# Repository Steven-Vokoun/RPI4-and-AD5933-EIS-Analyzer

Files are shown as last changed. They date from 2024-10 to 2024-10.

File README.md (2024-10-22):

# RPI4 and AD5933 EIS Analyzer
Overview:
- Mostly functioning but needs improvements.
- Libraries for AD5933 and MUX's working at this time.
- GUI utilizes custom tkinter.
- Fitting utilized "Impedance" python library (planning to update for robustness)
- Automatic gain switching methods implemented, but has bugs

Improvements I need to make in the future:
- Implementation of the internal 5x switchable gains
- Shift screen off to the left hand side of the enclosure, so then the power supply can be placed right next to the analog board.  Also put filtering on the i2c lines.
- Configuration of 3 electrode switching with a double pole relay instead to completely get it out of the circuit
- Have an external calibration board to account for lead inductance and capacitance
- Add a warning for when the output is hitting supply rails

Future Goals:
- Switch off of a RPI, to a lower level board for lower power consumption
- Shrink the device
- Make my own battery management board

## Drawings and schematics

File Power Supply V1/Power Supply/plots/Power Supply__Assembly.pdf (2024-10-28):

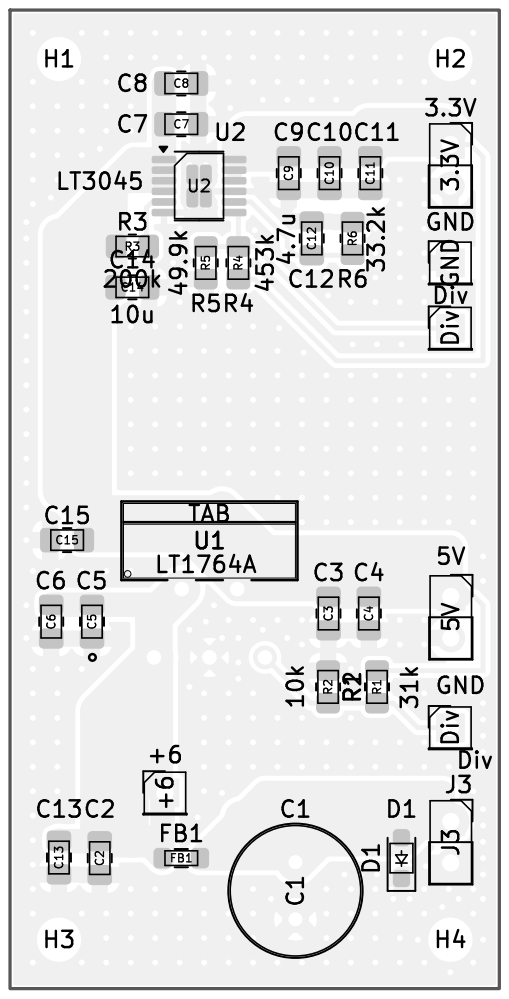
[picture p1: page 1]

Id: 1/1 Title: File: Power Supply.kicad_pcb Sheet:

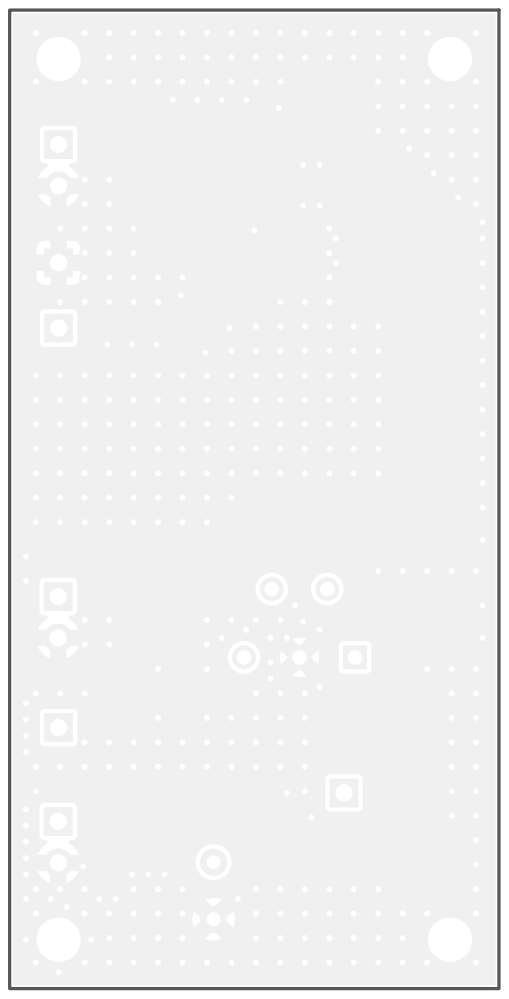
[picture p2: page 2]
D Date: KiCad; E.D.A. 8.0.2 Size: A4; Rev:

Id: 1/1 Title: File: Power Supply.kicad_pcb Sheet:

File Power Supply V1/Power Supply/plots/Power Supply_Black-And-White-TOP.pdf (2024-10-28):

FB1 | C4 C9 1 | 2 | 3 | 4 | 5 | 6 1 | 2 | 3 | 4 | 5 | 6 ABCD | ABCD Date: KiCad | E.D.A. 8.0.2 Size: A4 | Rev:


Id: 1/1 Title: File: Power Supply.kicad_pcb Sheet:

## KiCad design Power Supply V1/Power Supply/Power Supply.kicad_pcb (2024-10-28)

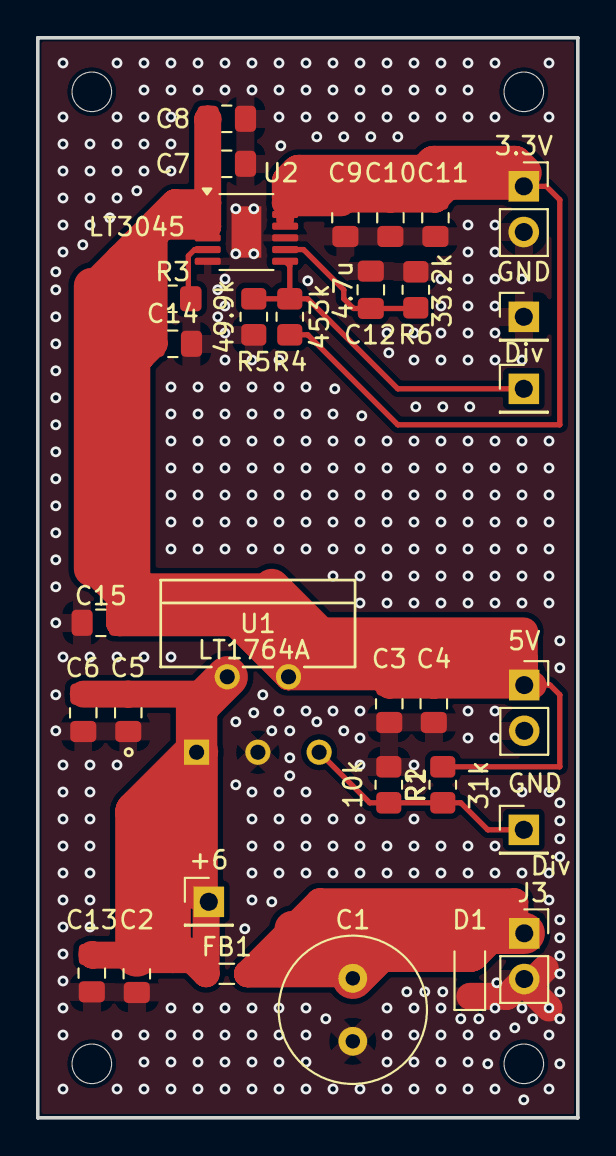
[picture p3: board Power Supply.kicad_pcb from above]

Board: 2 copper layers, 30.0 x 60.0 mm, 36 parts (0 on the bottom side), 9 nets.

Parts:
3.3V, 5V: Conn_01x02_Pin; PinSocket_1x02_P2.54mm_Vertical
+6: Conn_01x01_Pin; PinHeader_1x01_P2.54mm_Vertical
C1: 100u; C_Radial_D8.0mm_H11.5mm_P3.50mm
C2, C3, C8, C13: 22u; C_0805_2012Metric_Pad1.18x1.45mm_HandSolder
C4, C6, C7, C11: .1u; C_0805_2012Metric_Pad1.18x1.45mm_HandSolder
C5, C9, C10, C14, C15: 10u; C_0805_2012Metric_Pad1.18x1.45mm_HandSolder
C12: 4.7u; C_0805_2012Metric_Pad1.18x1.45mm_HandSolder
D1: CDSOD323-To8; D_SOD-323_HandSoldering
Div: Conn_01x01_Pin; PinHeader_1x01_P2.54mm_Vertical
Div#2: Conn_01x01_Pin; PinHeader_1x01_P2.54mm_Vertical
FB1: Ferrite; L_0805_2012Metric_Pad1.05x1.20mm_HandSolder
GND: Conn_01x01_Pin; PinHeader_1x01_P2.54mm_Vertical
H1, H2, H3, H4: MountingHole; MountingHole_2.2mm_M2
J3: Conn_01x02_Pin; PinSocket_1x02_P2.54mm_Vertical
R1: 31k; R_0805_2012Metric_Pad1.20x1.40mm_HandSolder
R2: 10k; R_0805_2012Metric_Pad1.20x1.40mm_HandSolder
R3: 200k; R_0805_2012Metric_Pad1.20x1.40mm_HandSolder
R4: 453k; R_0805_2012Metric_Pad1.20x1.40mm_HandSolder
R5: 49.9k; R_0805_2012Metric_Pad1.20x1.40mm_HandSolder
R6: 33.2k; R_0805_2012Metric_Pad1.20x1.40mm_HandSolder
U1: LT1764A; TO220-5_T_LIT
U2: LT3045; MSOP-12-1EP_3x4mm_P0.65mm_EP1.65x2.85mm

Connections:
+3.3V: 3.3V.1, C9.1, C10.1, C11.1, R4.1, U2.10 (OUTS), U2.11 (OUT), U2.12 (OUT)
+5V: 5V.1, C3.1, C4.1, C7.1, C8.1, C14.1, C15.1, R1.1, R3.1, U1.4 (OUT), U2.1 (IN), U2.2 (IN), U2.3 (IN), U2.4 (EN/UV)
+6V: +6.1, C2.1, C5.1, C6.1, C13.1, FB1.2, U1.1 (*SHDN), U1.2 (IN)
/Div_1: Div.1, R1.2, R2.1, U1.5 (SENSE/ADJ)
/Div_2: Div#2.1, R4.2, R5.1, U2.7 (PGFB)
GND: 3.3V.2, 5V.2, C1.2, C2.2, C3.2, C4.2, C5.2, C6.2, C7.2, C8.2, C9.2, C10.2, C11.2, C12.2, C13.2, C14.2, C15.2, D1.1 (A1), GND.1, J3.2, R2.2, R5.2, R6.2, U1.3 (GND), U2.6 (ILIM), U2.9 (GND), U2.13 (GND)
unnamed: R3.2, U2.5 (PG)
unnamed: C12.1, R6.1, U2.8 (SET)
VCC: C1.1, D1.2 (A2), FB1.1, J3.1

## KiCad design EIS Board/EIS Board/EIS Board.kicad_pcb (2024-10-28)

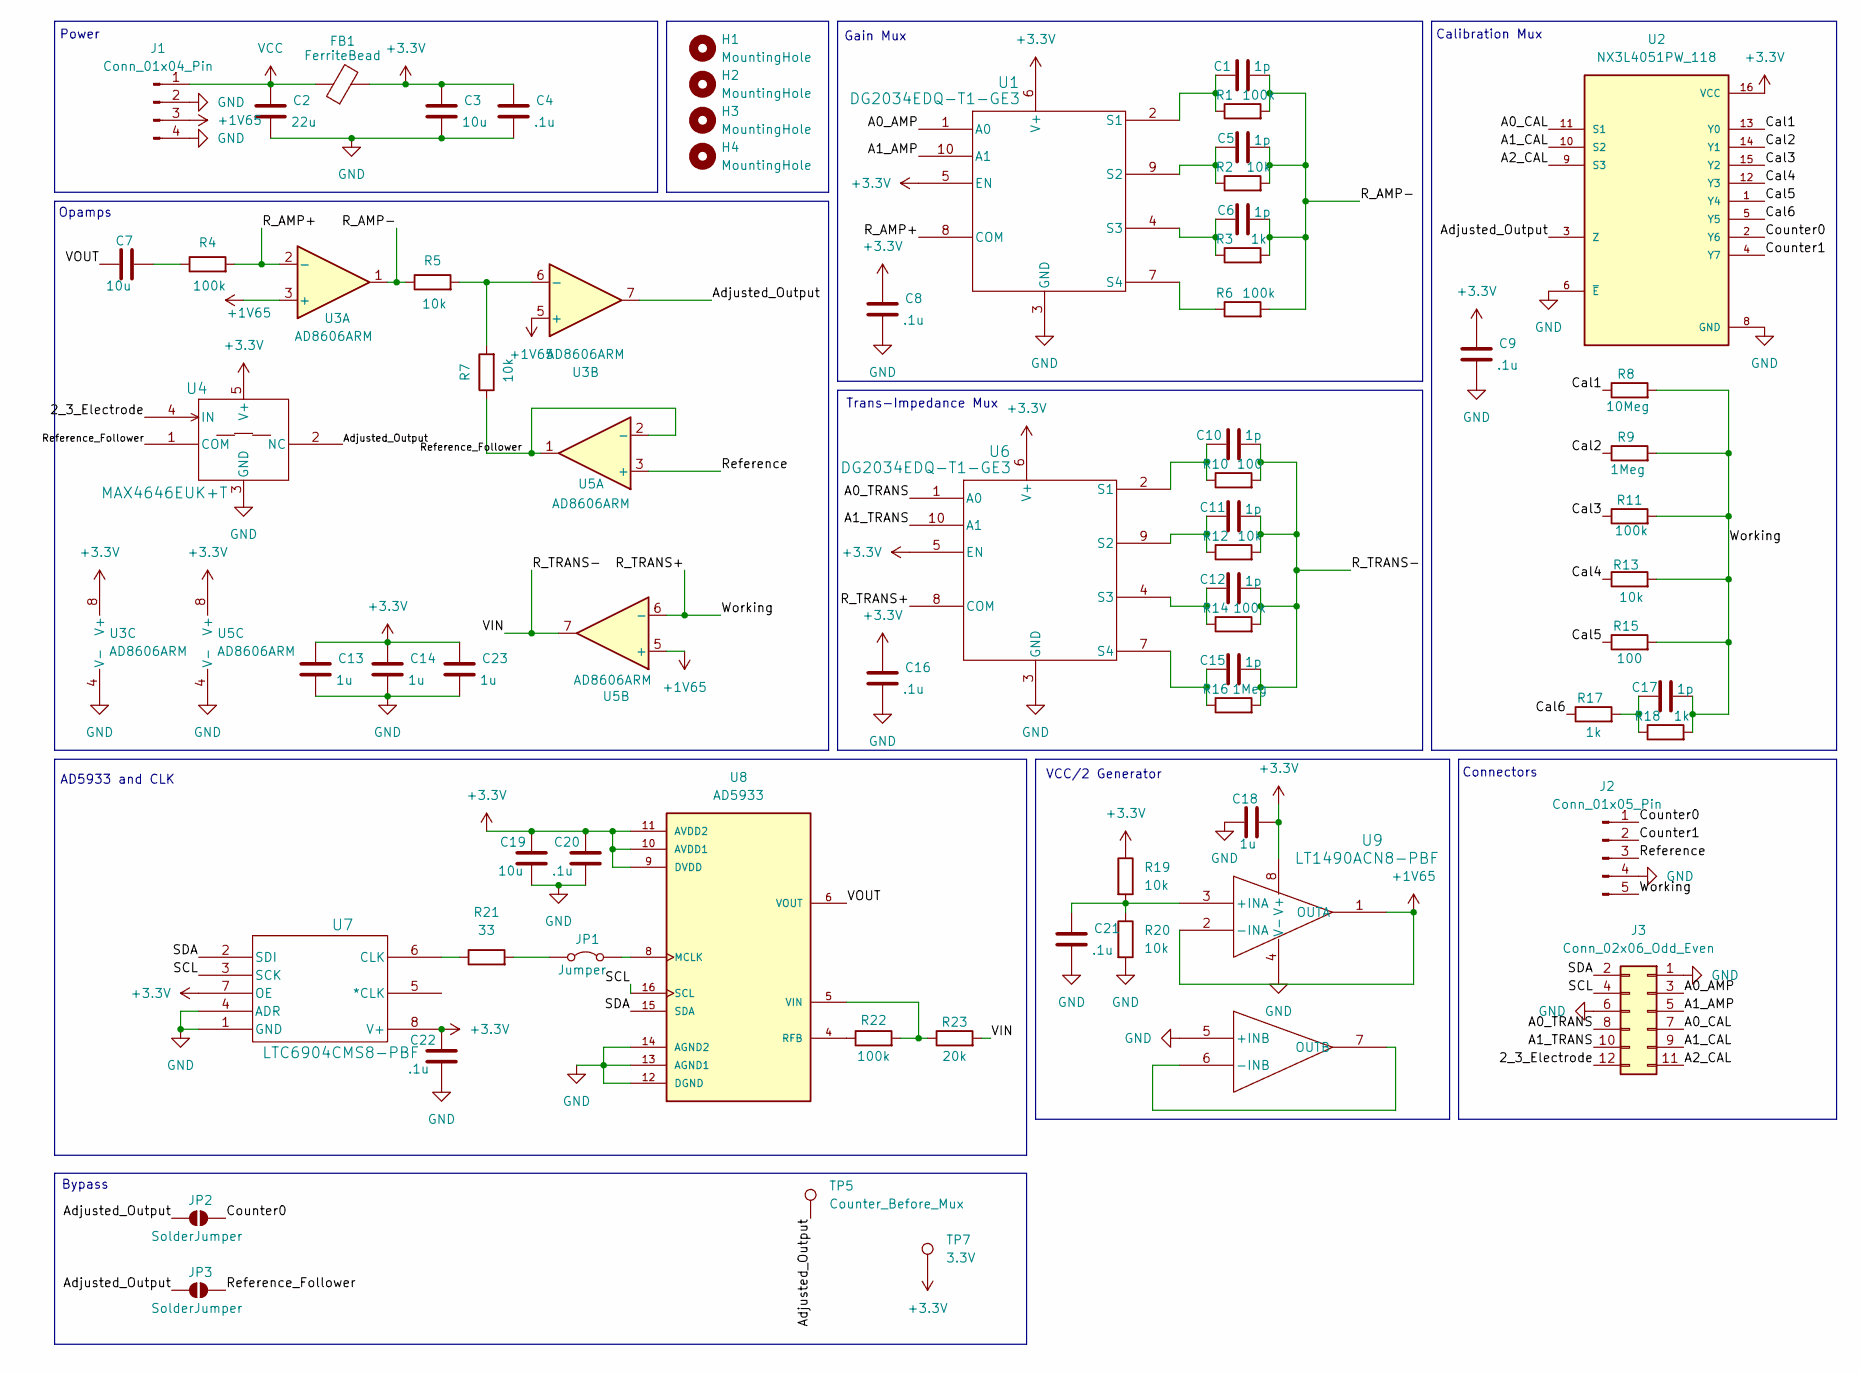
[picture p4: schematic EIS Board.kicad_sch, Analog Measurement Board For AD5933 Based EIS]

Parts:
C1, C5, C6, C10, C11, C12, C15, C17: 1p; C_0805_2012Metric_Pad1.18x1.45mm_HandSolder
C2: 22u; C_0805_2012Metric_Pad1.18x1.45mm_HandSolder
C3, C7, C19: 10u; C_0805_2012Metric_Pad1.18x1.45mm_HandSolder
C4, C8, C9, C16, C20, C21, C22: .1u; C_0805_2012Metric_Pad1.18x1.45mm_HandSolder
C13, C14, C18, C23: 1u; C_0805_2012Metric_Pad1.18x1.45mm_HandSolder
FB1: FerriteBead; L_0805_2012Metric_Pad1.05x1.20mm_HandSolder
H1, H2, H3, H4: MountingHole; MountingHole_2.2mm_M2
J1: Conn_01x04_Pin; PinHeader_1x04_P2.54mm_Vertical
J2: Conn_01x05_Pin; PinHeader_1x05_P2.54mm_Vertical
J3: Conn_02x06_Odd_Even; PinHeader_2x06_P2.54mm_Vertical
JP1: Jumper; TestPoint_2Pads_Pitch2.54mm_Drill0.8mm
JP2, JP3: SolderJumper; SolderJumper-2_P1.3mm_Open_RoundedPad1.0x1.5mm
R1, R4, R6, R11, R14, R22: 100k; R_0805_2012Metric_Pad1.20x1.40mm_HandSolder
R2, R5, R7, R12, R13, R19, R20: 10k; R_0805_2012Metric_Pad1.20x1.40mm_HandSolder
R3, R17, R18: 1k; R_0805_2012Metric_Pad1.20x1.40mm_HandSolder
R8: 10Meg; R_0805_2012Metric_Pad1.20x1.40mm_HandSolder
R9, R16: 1Meg; R_0805_2012Metric_Pad1.20x1.40mm_HandSolder
R10, R15: 100; R_0805_2012Metric_Pad1.20x1.40mm_HandSolder
R21: 33; R_0805_2012Metric_Pad1.20x1.40mm_HandSolder
R23: 20k; R_0805_2012Metric_Pad1.20x1.40mm_HandSolder
TP5: Counter_Before_Mux; TestPoint_Loop_D1.80mm_Drill1.0mm_Beaded
TP7: 3.3V; TestPoint_Loop_D1.80mm_Drill1.0mm_Beaded
U1, U6: DG2034EDQ-T1-GE3; SMT_EDQ-T1-GE3_VIS
U2: NX3L4051PW_118; SOP65P640X110-16N; PARTREV 5, 3 July 2012
U3, U5: AD8606ARM; MSOP-8_3x3mm_P0.65mm
U4: MAX4646EUK+T; 21-0057F_MXM
U7: LTC6904CMS8-PBF; MSOP-8_MS_LIT
U8: AD5933; SOP65P780X200-16N; PARTREV F
U9: LT1490ACN8-PBF; PDIP-8_N_LIT

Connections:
+1V65: J1.3, U3.3 (+), U3.5 (+), U5.5 (+), U9.1 (OUTA), U9.2 (-INA)
+3.3V: C3.1, C4.1, C8.1, C9.1, C13.1, C14.1, C16.1, C18.2, C19.1, C20.1, C22.1, C23.1, FB1.2, R19.1, TP7.1, U1.5 (EN), U1.6 (V+), U2.16 (VCC), U3.8 (V+), U4.5 (V+), U5.8 (V+), U6.5 (EN), U6.6 (V+), U7.7 (OE), U7.8 (V+), U8.9 (DVDD), U8.10 (AVDD1), U8.11 (AVDD2), U9.8 (V+)
/2_3_Electrode: J3.12, U4.4 (IN)
/A0_AMP: J3.3, U1.1 (A0)
/A0_CAL: J3.7, U2.11 (S1)
/A0_TRANS: J3.8, U6.1 (A0)
/A1_AMP: J3.5, U1.10 (A1)
/A1_CAL: J3.9, U2.10 (S2)
/A1_TRANS: J3.10, U6.10 (A1)
/A2_CAL: J3.11, U2.9 (S3)
/Adjusted_Output: JP2.1 (A), JP3.1 (A), TP5.1, U2.3 (Z), U3.7, U4.2 (NC)
/Cal1: R8.1, U2.13 (Y0)
/Cal2: R9.1, U2.14 (Y1)
/Cal3: R11.1, U2.15 (Y2)
/Cal4: R13.1, U2.12 (Y3)
/Cal5: R15.1, U2.1 (Y4)
/Cal6: R17.1, U2.5 (Y5)
/Counter0: J2.1, JP2.2 (B), U2.2 (Y6)
/Counter1: J2.2, U2.4 (Y7)
/R_AMP+: R4.2, U1.8 (COM), U3.2 (-)
/R_AMP-: C1.2, C5.2, C6.2, R1.2, R2.2, R3.2, R5.1, R6.2, U3.1
/R_TRANS+: C17.2, J2.5, R8.2, R9.2, R11.2, R13.2, R15.2, R18.2, U5.6 (-), U6.8 (COM)
/R_TRANS-: C10.2, C11.2, C12.2, C15.2, R10.2, R12.2, R14.2, R16.2, R23.2, U5.7
/Reference: J2.3, U5.3 (+)
/Reference_Follower: JP3.2 (B), R7.1, U4.1 (COM), U5.1, U5.2 (-)
/SCL: J3.4, U7.3 (SCK), U8.16 (SCL)
/SDA: J3.2, U7.2 (SDI), U8.15 (SDA)
/VOUT: C7.1, U8.6 (VOUT)
GND: C2.2, C3.2, C4.2, C8.2, C9.2, C13.2, C14.2, C16.2, C18.1, C19.2, C20.2, C21.2, C22.2, C23.2, J1.2, J1.4, J2.4, J3.1, J3.6, R20.2, U1.3 (GND), U2.6 (~E), U2.8 (GND), U3.4 (V-), U4.3 (GND), U5.4 (V-), U6.3 (GND), U7.1 (GND), U7.4 (ADR), U8.12 (DGND), U8.13 (AGND1), U8.14 (AGND2), U9.4 (V-), U9.5 (+INB)
unnamed: C7.2, R4.1
unnamed: C17.1, R17.2, R18.1
unnamed: JP1.1 (A), R21.2
unnamed: JP1.2 (B), U8.8 (MCLK)
unnamed: C1.1, R1.1, U1.2 (S1)
unnamed: C5.1, R2.1, U1.9 (S2)
unnamed: C6.1, R3.1, U1.4 (S3)
unnamed: R6.1, U1.7 (S4)
unnamed: R5.2, R7.2, U3.6 (-)
unnamed: C10.1, R10.1, U6.2 (S1)
unnamed: C11.1, R12.1, U6.9 (S2)
unnamed: C12.1, R14.1, U6.4 (S3)
unnamed: C15.1, R16.1, U6.7 (S4)
unnamed: R21.1, U7.6 (CLK)
unnamed: R22.1, U8.4 (RFB)
unnamed: R22.2, R23.1, U8.5 (VIN)
unnamed: C21.1, R19.2, R20.1, U9.3 (+INA)
unnamed: U9.6 (-INB), U9.7 (OUTB)
VCC: C2.1, FB1.1, J1.1

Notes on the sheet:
Opamps
AD5933 and CLK
VCC/2 Generator
Power
Bypass
Gain Mux
Calibration Mux
Trans-Impedance Mux
Connectors

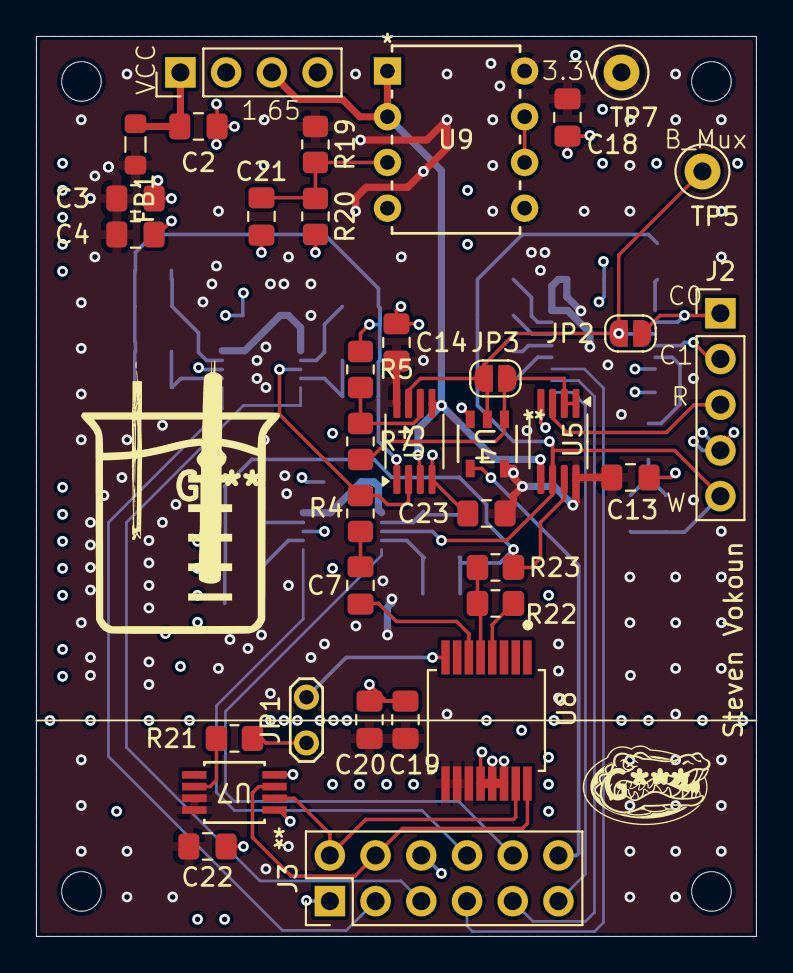
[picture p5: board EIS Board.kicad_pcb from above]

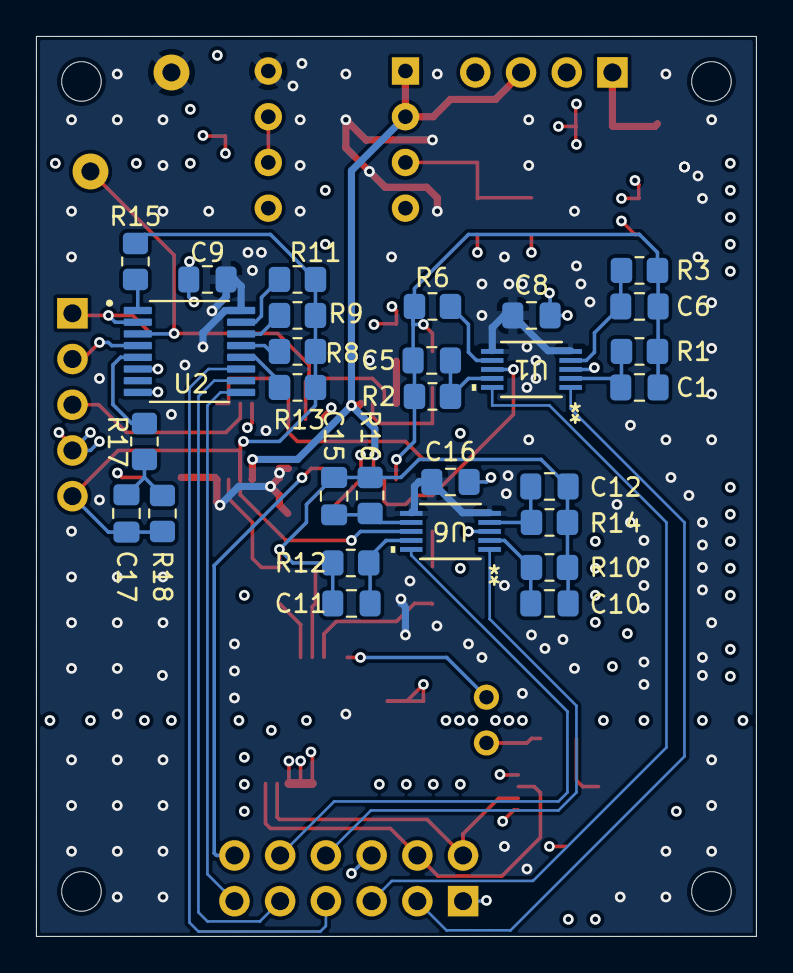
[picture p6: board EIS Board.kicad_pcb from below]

Board: 4 copper layers, 40.0 x 50.0 mm, 68 parts (29 on the bottom side), 48 nets.

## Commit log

2024-07-21 added some automatic gain switching and advanced calibration. binary search not yet implemented.
2024-07-21 set output voltage
2024-07-21 edited calibration gain
2024-07-21 put back in the test and 3 electrode instead of 2
2024-07-24 added calibration class for easier management
2024-07-24 changes to find impedance from voltage function. needs testing
2024-07-31 2 electrode to remove oscillation
2024-08-09 debugging prints
2024-08-09 additional debugging prints
2024-10-28 addded schematics
    [EIS Board-B_Cu.gbr, EIS Board-B_Mask.gbr, EIS Board-B_Silks.gbr, EIS Board-Edge_Cuts.gbr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]
